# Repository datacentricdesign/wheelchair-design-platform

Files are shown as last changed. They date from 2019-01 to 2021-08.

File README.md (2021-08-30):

# [Wheelchair Design Platform](https://datacentricdesign.github.io/wheelchair-design-platform/)

Welcome!

This repository contains some resources to help designers and developers speak the same language, and work together towards addressing relevant challenges for wheelchair users. It is a collection of workshop materials, code examples and also a compilation of resources to foster a prospering research and design community around wheelchair users.

The best way to explore this repository is through the GitHub Page website: [right here!](https://datacentricdesign.github.io/wheelchair-design-platform/)

# Contributors

Thank you to all the contributors of this project!

(https://github.com/Ryudas)
(https://github.com/dhavalshah02)
(https://github.com/Kattthii)
(https://github.com/jackybourgeois)
(https://github.com/emiliaingemarsdotter)
(https://github.com/cprecioso)
(https://github.com/livein21st)
(https://github.com/gomezago)

# Existing projects

* [The hiking wheelchair](https://github.com/cprecioso/wheelchair-design-platform)
* [The EDU wheelchair](https://github.com/ctsai-1/wheelchair-design-platform)
* [Weelchair tracking for basketball players](https://github.com/FabianIDE/wheelchair-design-platform)
* [Disco Wheelchair](https://github.com/MatthijsBrem/wheelchair-design-platform)
* [Wheelchair Madness 2222](https://github.com/pherkan/wheelchair-design-platform/tree/master/wheelchair)
* [Who is sitting?](https://github.com/Rosanfoppen/wheelchair-design-platform/tree/master/wheelchair)
* [Magic Wheelchair](https://github.com/Yuciena/wheelchair-design-platform)
* [Yoga Wheelchair](https://github.com/artgomad/wheelchair-design-platform)

Feel free to contact us at jacky@datacentricdesign.org. We welcome feedback, pull requests
or links to your project.

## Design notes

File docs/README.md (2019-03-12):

Wheelchair Design Platform is a repository that contains some resources to help
designers and developers speak the same language, and work together towards
addressing relevant challenges for wheelchair users. It is a collection of
workshop materials, code examples and also a compilation of resources to foster
a prospering research and design community around wheelchair users.

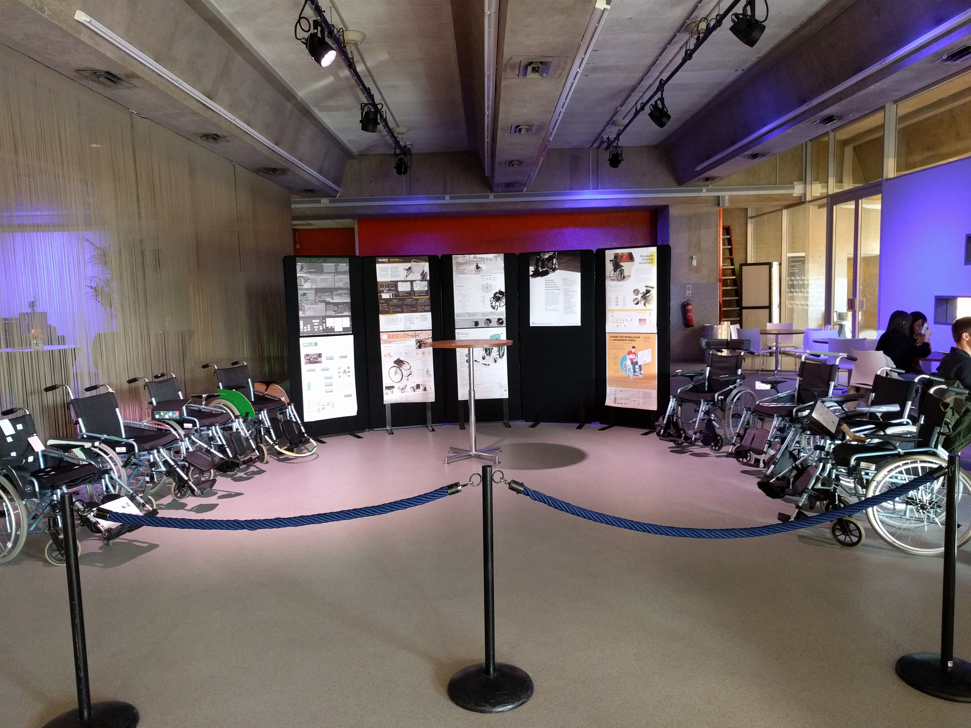
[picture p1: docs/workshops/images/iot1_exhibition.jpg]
IoT1 Exhibition


## Workshops

* [Getting started](workshops/GettingStarted.md)
* [Workshop 1: Building an Internet-Connected Wheelchair](workshops/Workshop1.md)
* [Workshop 2: Integrating and Visualising Sensor-Based Data](workshops/Workshop2.md)
* [Workshop 3: Developing Algorithms and Controlling Actuators](workshops/Workshop3.md)
* [Workshop 4: Developing and Conducting a Data Collection Campaign](workshops/Workshop4.md)
* [Workshop 5: Implementing a Machine Learning Pipeline](workshops/Workshop5.md)
* [Workshop 6: Developing a Product Analytics Dashboard](workshops/Workshop6.md)

## Resources

* This platform uses two programming languages, Python on computers and C on
micro-controllers. While descriptions and examples of code should help you
get started, you can find some additional resources
[here](resources/software.md).

* Documentation of your project is key,
[here are some tips and examples](resources/documentation.md).

* [Git manipulation such as Pull Requests](resources/git.md).

## Main Components

__**Disclaimer:**__ the design of this platform focuses on flexibility and
technology exploration rather than optimization\.

The main design includes a Raspberry Pi 3 and an Arduino Mega 2560 on the wheelchair frame.

The Arduino Mega is the micro-controller of the platform. Fixed on the main frame of the wheelchair,
it can collect data from sensors (e.g. force sensors, accelerometers), and trigger actions from actuators
(e.g. LEDs, vibration motors).

More on the Arduino Mega can be found [here](resources/arduino.md "Arduino resources").

Raspberry Pi is a small computer. It is also fixed to the main frame of the wheelchair,
where it can:
* interact with the Arduino Mega via USB to receive data and transmit commands;
* interact with the Internet to transmit commands and receive data;
* store data locally in files;
* run (machine learning) algorithms.

More on the Raspberry Pi can be found [here](resources/raspberrypi.md "Raspberry Pi resources").

These components fit together as shown on the following diagram. A large powerbank
powers the Raspberry Pi. The Arduino Mega communicates and receives power from the
Raspberry Pi via USB. A Feather (Arduino-like development board) on the wheel connects to
the Raspberry Pi via Bluetooth to sense and actuate from the wheel.

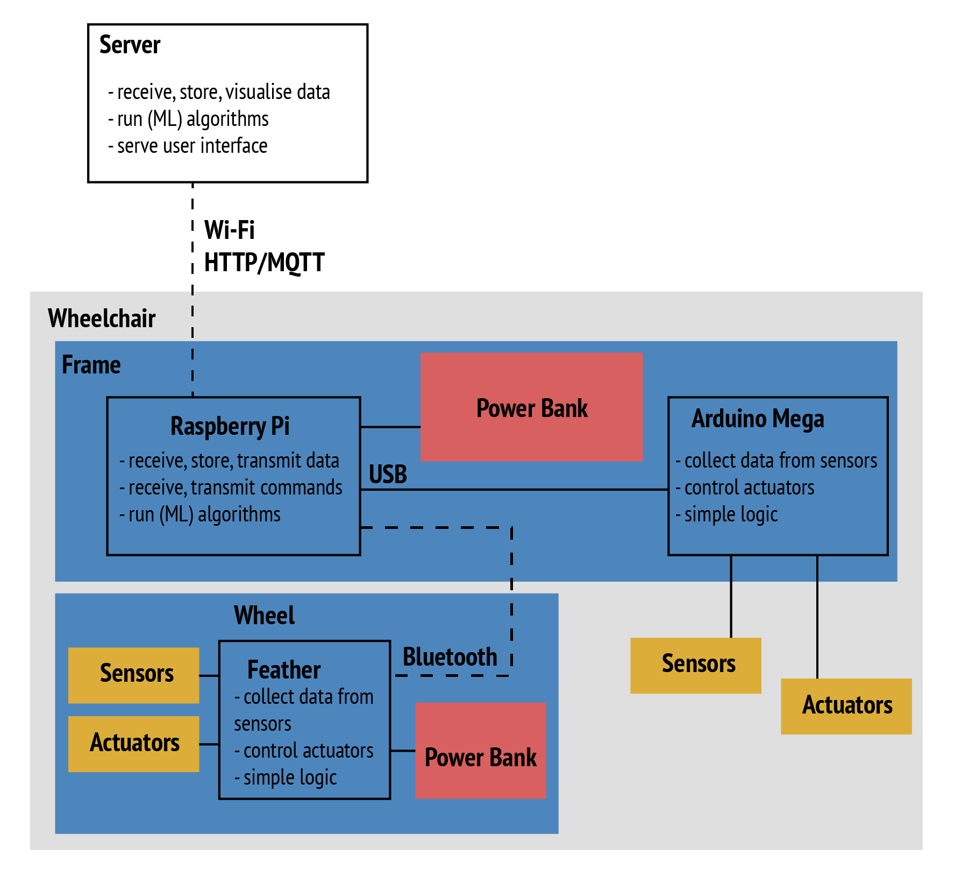
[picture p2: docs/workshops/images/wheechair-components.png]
Main Wheelchair components


## List of suggested components:

On the frame:

* 1 Raspberry Pi 3B+;
* 1 SD card (Some come directly with NOOBS installed);
* 1 Arduino Mega;
* 1 Large power bank;
* 1 large breadboard;
* 1 USB cable A/micro (Powerbank to Raspberry Pi);
* 1 USB cable A/B (Raspberry Pi to Arduino Mega).

On the wheel:

* 1 Feather 32u4 (Bluetooth enabled);
* 1 small power bank;
* 1 small breadboard;
* 1 USB cable A/B (power bank to Arduino Uno).

## Contact and Existing projects

* [The hiking wheelchair](https://github.com/cprecioso/wheelchair-design-platform)
* [The EDU wheelchair](https://github.com/ctsai-1/wheelchair-design-platform)
* [Weelchair tracking for basketball players](https://github.com/FabianIDE/wheelchair-design-platform)
* [Disco Wheelchair](https://github.com/MatthijsBrem/wheelchair-design-platform)
* [Wheelchair Madness 2222](https://github.com/pherkan/wheelchair-design-platform/tree/master/wheelchair)
* [Who is sitting?](https://github.com/Rosanfoppen/wheelchair-design-platform/tree/master/wheelchair)
* [Magic Wheelchair](https://github.com/Yuciena/wheelchair-design-platform)
* [Yoga Wheelchair](https://github.com/artgomad/wheelchair-design-platform)

Feel free to contact us at jacky@datacentricdesign.org. We welcome feedback, pull requests
or links to your project.

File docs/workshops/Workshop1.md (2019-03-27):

# Workshop 1: Building an Internet-connected Wheelchair

In this workshop we lead you step-by-step toward setting up the main components
of the Internet-Connected Wheelchair by getting the code, registering on the cloud
platform, running a Python code and running an Arduino code.

1. [Git Flow](#1-git-flow)
2. [Data-Centric Data Hub](#2-data-centric-design-hub-per-group)
3. [Run Python Example](#3-run-python-example)
4. [Data Collection with Arduino](#4-data-collection-with-arduino)
5. [Setting up the Raspberry Pi](#5-setting-up-the-raspberry-pi)

# 1 Git Flow

### 1.1 Fork Wheelchair Design Platform repository (only one member of the group)

*'A fork is a copy of a repository. Forking a repository allows you to freely
experiment with changes without affecting the original project.'*
<a href="https://help.github.com/articles/fork-a-repo/" target="_blank">(GitHub Help)</a>

Go to the GitHub repository of the Wheelchair Design Platform:
<a href="https://github.com/datacentricdesign/wheelchair-design-platform" target="_blank">https://github.com/datacentricdesign/wheelchair-design-platform</a>

On the top-right corner of this GitHub page, click on Fork.

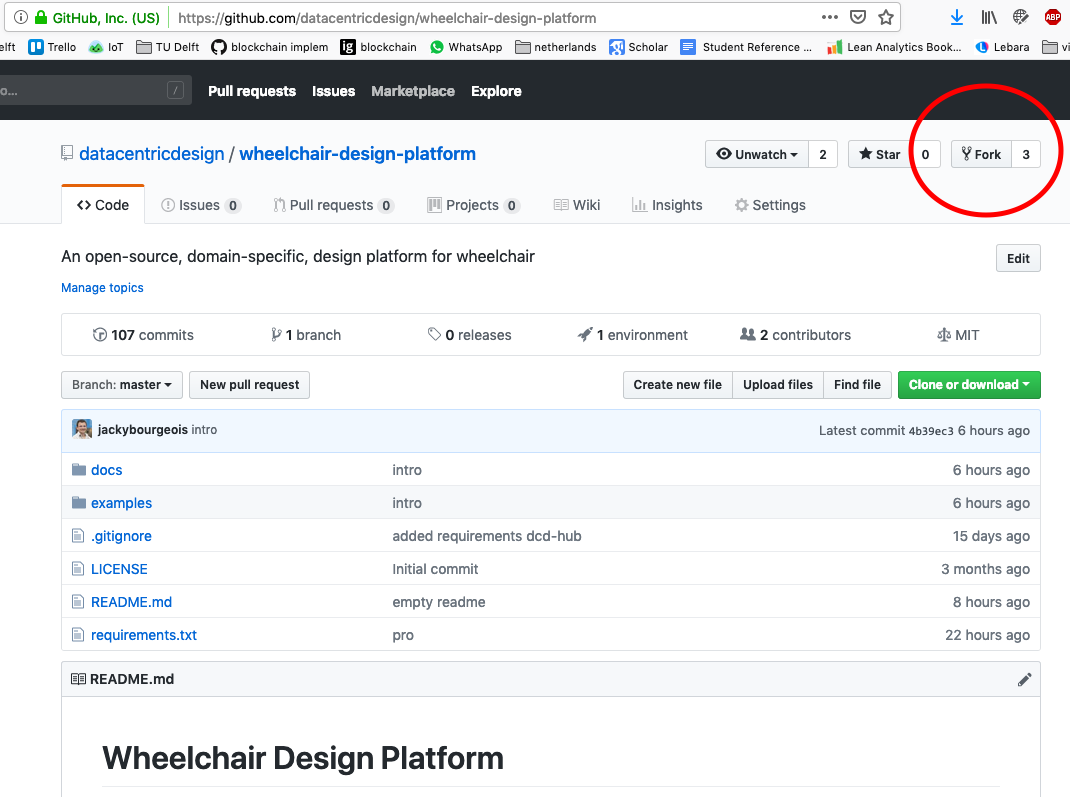
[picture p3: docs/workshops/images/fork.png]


In the dialog, select your account (where you create the copy of the repository).

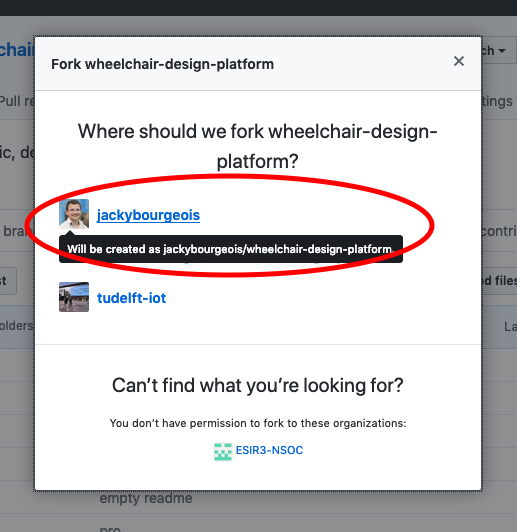
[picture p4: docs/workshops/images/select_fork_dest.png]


You now have a copy of the wheelchair-design-platform repository on your own account.

### 1.2 Add members to repo (only one member of the group)

Your repository is publicly accessible for reading. However, you need to give
the other members of the group access to this repository. On the top menu, click
*'Settings' > 'Collaborators'*. Search the username of your group members and add them.

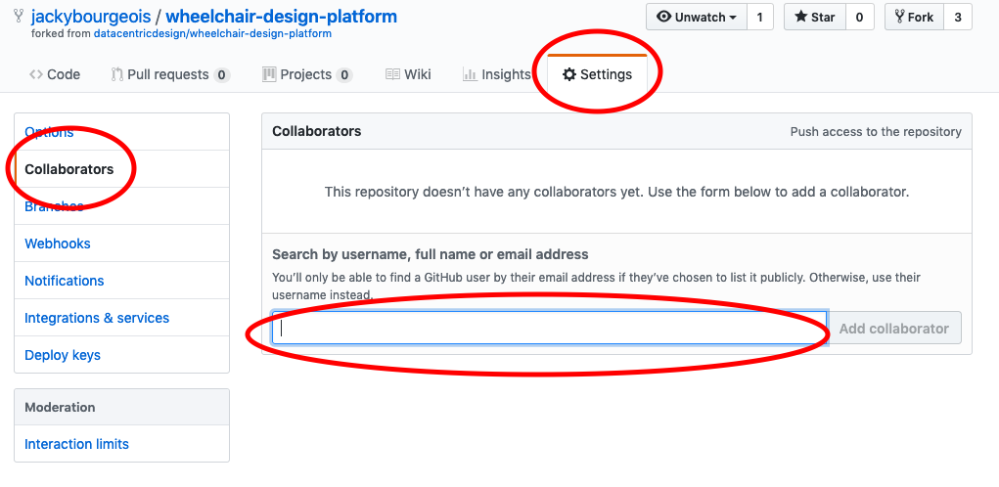
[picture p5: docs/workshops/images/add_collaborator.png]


### 1.3 Create a project (only one member of the group)

GitHub offers a convenient way of managing your projects with a Kanban (scheduling system) style
board. On the top menu, click on 'Projects' and click on the green button 'New
Project'. Fill in a project name, select the template 'Basic Kanban' and click
'Create project'. You can use this space to map your tasks and your progress.

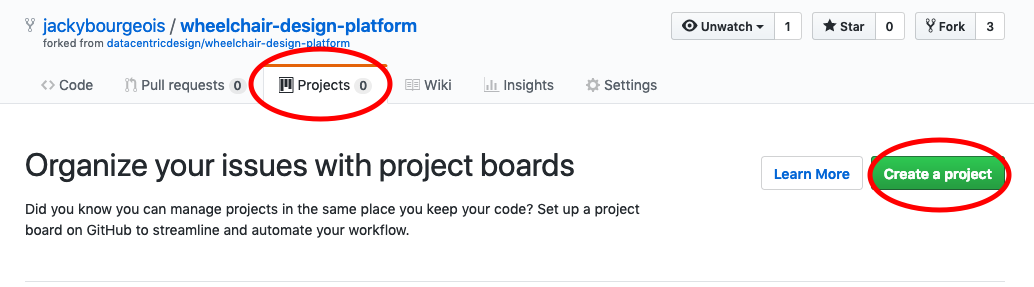
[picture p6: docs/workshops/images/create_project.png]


### 1.4 Clone repository (all group members)

*'When you create a repository on GitHub, it exists as a remote repository. You
can clone your repository to create a local copy on your computer and sync
between the two locations.'*
<a href="https://help.github.com/articles/cloning-a-repository/" target="_blank">(GitHub Help)</a>

On GitHub, at the top of your forked repository, click on the green button 'Clone or
download' and copy the provided link.

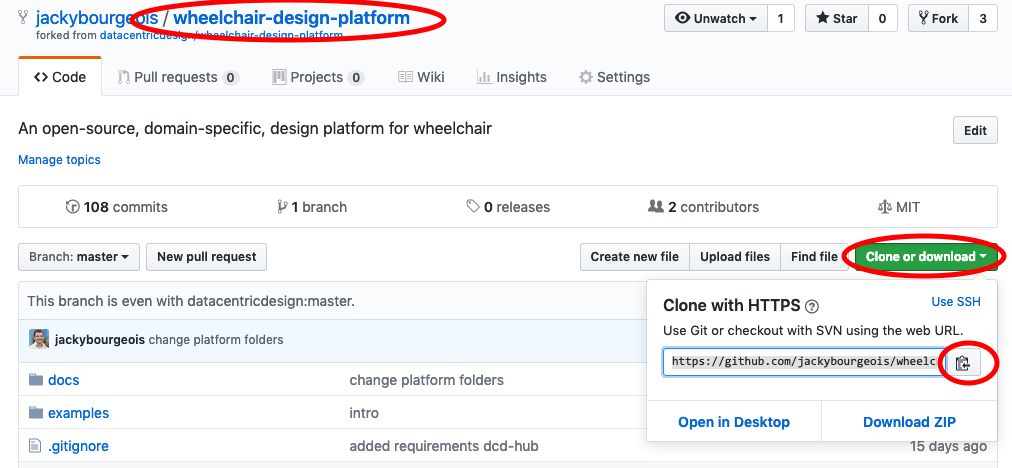
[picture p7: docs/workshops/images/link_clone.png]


Go back to the Atom terminal, and type 'git clone' followed by the link you copied.
For example:

```bash
git clone https://github.com/example/wheelchair-design-platform.git
```

Flowchart Push Button

Let's tell Git who we are, by typing the following commands (enter these commands one after the other):

```bash
git config --global user.email "YOUR EMAIL ADDRESS"
git config --global user.name "YOUR NAME"
```

## 1.5 Project in Atom

To open the project you cloned, click on 'File' > 'Open Folder' on the top menu and
select the folder you cloned. On the left panel, you can see the files of your
project.

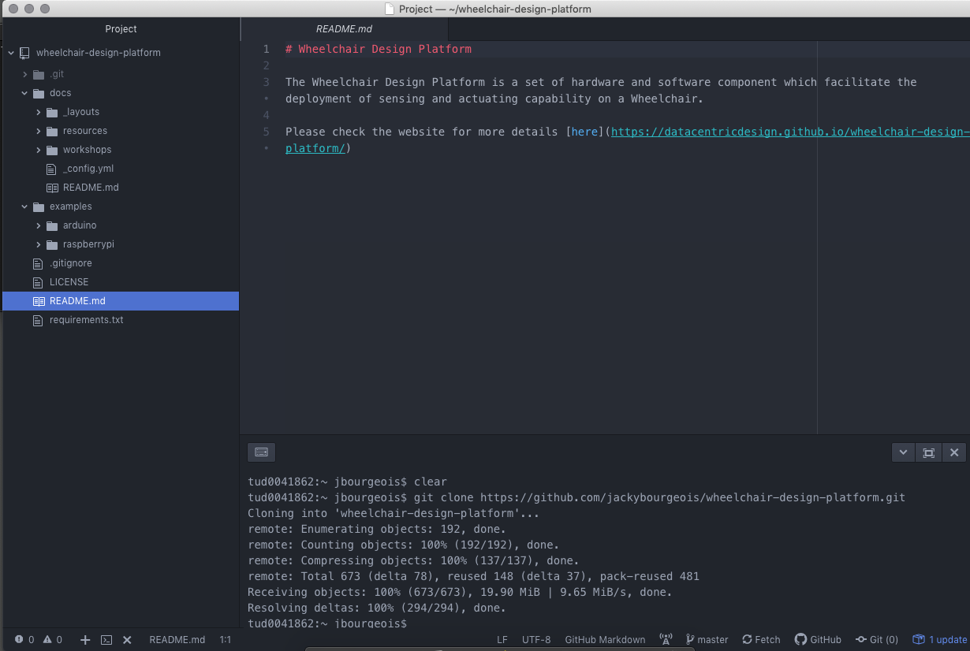
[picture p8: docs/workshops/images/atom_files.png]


Let's have a closer look:

* The .git folder contains the full history of your project, managed by git. Do not
edit or delete files in this folder;
* The docs folder contains documentation and workshops;
* examples contains all code examples to get started;
* .gitignore contains the list of files/file extensions you do not want to track
with Git. It is especially convenient for local configuration or passwords not
to be shared;
* LICENSE contains the MIT license for this project;
* README.md contains a short introduction to the platform in Markdown. Markdown
is a lightweight markup language, i.e. minimal set tags to format text;
* requirements.txt contains the list of the python libraries you need to install for
the project to work;

## 1.6 Sign up on the Data-Centric Design Hub

We now want to register an account for a cloud service. We will use the prototype
from TU Delft IDE's Faculty of the Data-Centric Design Hub. Go to <a href="https://dwd.tudelft.nl/manager" target="_blank">https://dwd.tudelft.nl/manager</a>

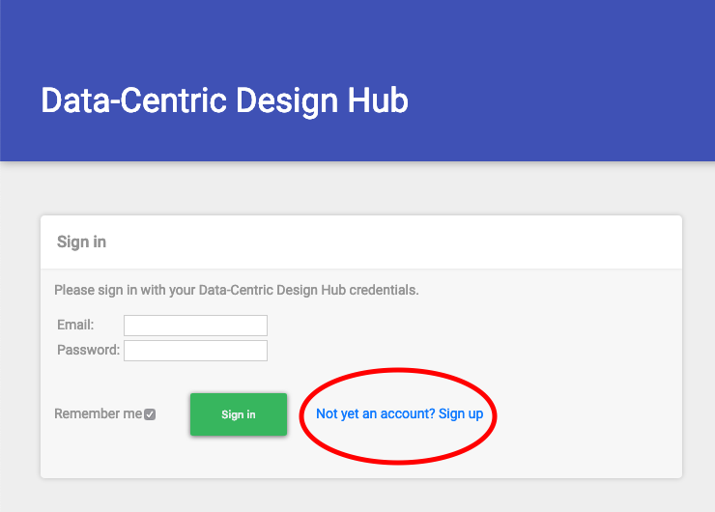
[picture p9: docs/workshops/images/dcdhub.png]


Sign up as a group with an email address, a name and a password.

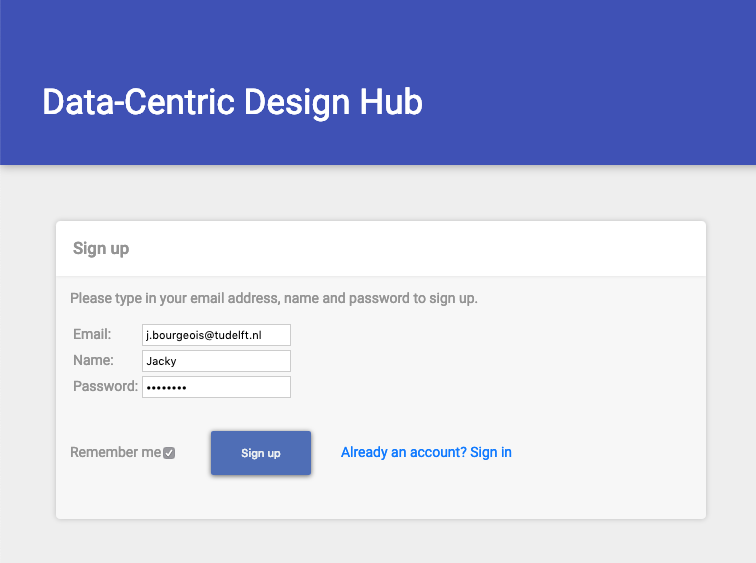
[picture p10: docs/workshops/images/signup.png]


The sign up process creates an account, then the standard OAuth2 process starts
with a consent: you need to let the manager access your Things, so that it can
help you manage them. To do so click "Allow access".

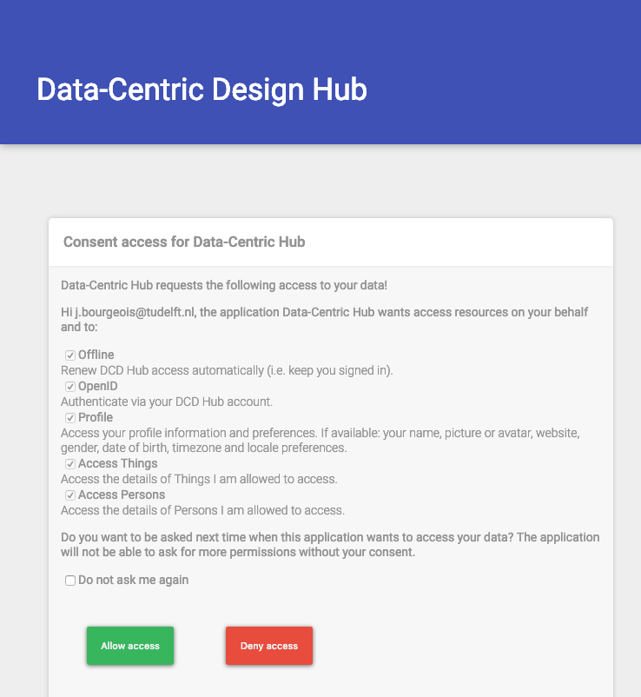
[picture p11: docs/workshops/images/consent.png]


Once the consent succeeded, you can click on 'My Things' and create a first one.
For example with the name 'My wheelchair', type 'Wheelchair', and a
description 'An Internet-connected wheelchair'.

The process may take a few seconds, as the hub generates an access token for your Thing.

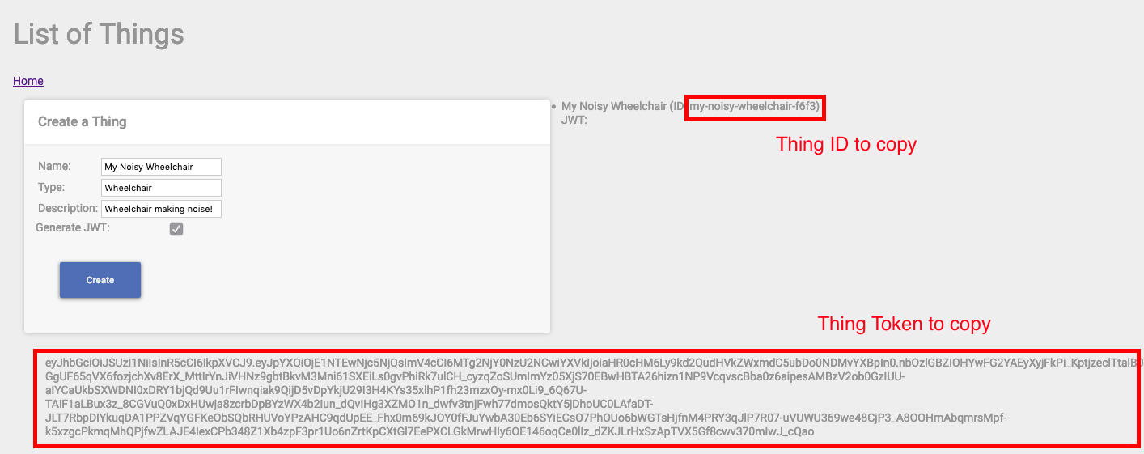
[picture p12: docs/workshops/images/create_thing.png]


**COPY AND SAVE THIS TOKEN** in a text file, it will be shown only once and enables
your wheelchair to communicate with the hub. You can also save the thing id, but
you can always go back to the manager to retrieve this id.

Back to Atom and your project, let's create a first Python example.

## 3 Run Python Example

### 3.1 Dependencies

We use Pip to install the dependencies we need, listed in the file requirements.txt.
This file contains a dependence to the library writen for the Data-Centric Design
Hub as well as the a dependence for MQTT, a communication protocol we use to
talk to the hub.

Open the Atom terminal ('plus' sign in the bottom-left corner) and execute the following command.

On Mac:

```bash
pip3 install -r requirements.txt --user
```
On Windows:

```bash
python -m pip install -r requirements.txt --user
```

Here we 'install' the Python dependencies for our project. The option -r indicates we provide a file name that contains
the required dependencies, the option --user indicates we install the dependencies
in a dependency folder specific for the current users.

## 3.2 Environment Variables

On the left panel, right-click on the root folder "wheelchair-design-platform" > New Folder and name it 'wheelchair'.

Copy the file examples > raspberrypi > get_started.py
in your 'wheelchair' folder.

Opening this file, this Python code import the necessary library, then we can see
the following lines:

```python
THING_ID = os.environ['THING_ID']
THING_TOKEN = os.environ['THING_TOKEN']
```

In Python, it means we look at the environment variables to read the id and
access token of our thing. To provide these information as environment variable,
right click at the root of your project (left panel) and create a file '.env'.

In this file, type in the following and paste your id and access token after
the equal signs.

```bash
THING_ID=
THING_TOKEN=
```

Note: We do not want to track the file '.env' with Git as it contains secrets. To
avoid any mistake, the file .gitignore list all files, folders and extensions to
ignore. You will find '.env' in the list.

## 3.3 Read through the Python Code

Going back to the get_started.py Python script, read through the code and comments
to capture the main steps:

* Create and connect a Thing to the Hub
* Retrieve and display the Thing details
* If the Thing is not containing any property, create a dumb property
* In any case, retrieve this dumb property
* Continuously call a method that generate dumb data and send them to the hub

Here are a few Python elements to note:

* Use # in Python to comment your code
* my_thing and my_property are variables
* To display information in the terminal, we use the method print()

```python
print("show text")
```

* Conditional statement: In Python we express the condition with 'if', elif
(else if) and else (more details
<a href="https://www.tutorialspoint.com/python/python_if_else.htm" target="_blank">here</a>.

In our case, we check if the thing details we retrieved from the server has no property
(a newly created Thing) and then create a dumb property.

```python
if len(my_thing.properties) == 0:
    # create a dumb property
```

* Indentation is key in Python. Take the previous example of condition, the indentation
defines what is in the condition. Any following line aligned with the if would be
considered outside the condition.

## 3.4 Execute the Python code

Let's execute this code. Go to the Atom terminal and type in the following command:

On Mac:

```bash
python3 wheelchair/get_started.py
```

On Windows:

```bash
python wheelchair\get_started.py
```

If the example runs properly you should see a log generated every two seconds,
indicating dumb data is being sent to the Hub.

## 3.5 Visualise Data on Grafana

To visualise this data, we use Grafana.

Go to the <a href="https://dwd.tudelft.nl/grafana" target="_blank">dwd.tudelft.nl/grafana</a>,
sign in with the provided login and password.

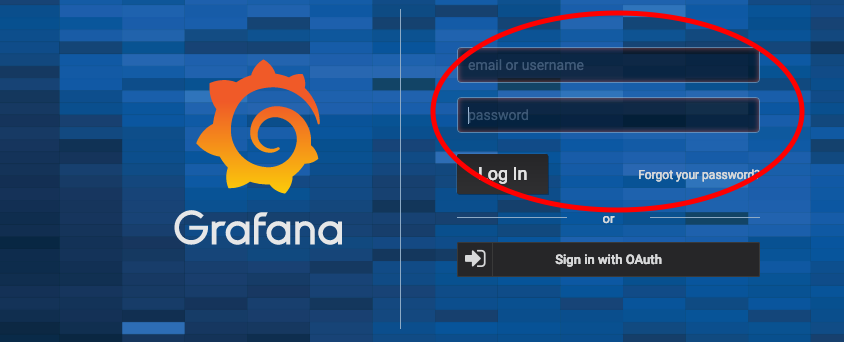
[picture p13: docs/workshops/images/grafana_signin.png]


Click on the plus on the left panel.

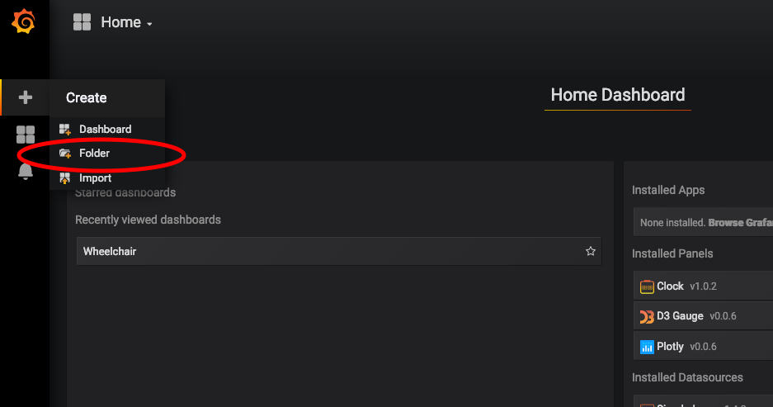
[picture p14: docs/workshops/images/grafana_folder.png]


Create a new folder for your project.

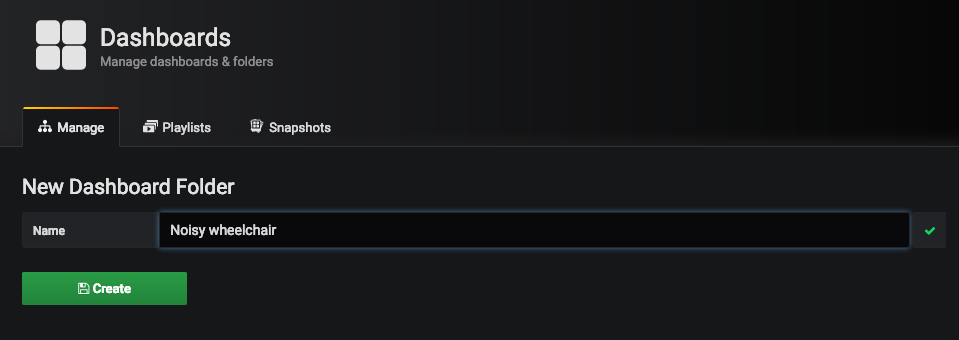
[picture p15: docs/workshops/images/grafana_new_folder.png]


Then, click on the green button 'New Dashboard' to create a new Dashboard, and
select a new panel 'Graph'.

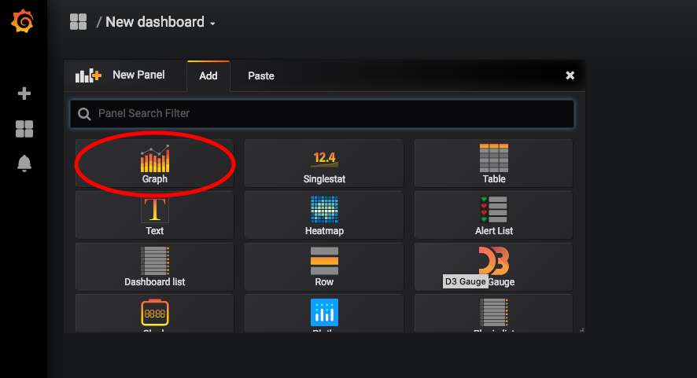
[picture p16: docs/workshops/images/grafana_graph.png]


At the top of this new panel, click on 'Panel Title > Edit'

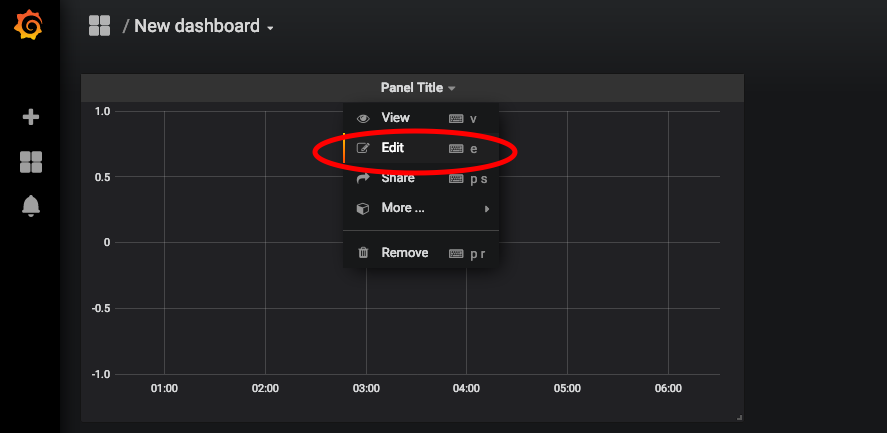
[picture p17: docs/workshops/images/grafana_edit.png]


At the bottom, in the query element GROUP BY, click on time and 'remove'.

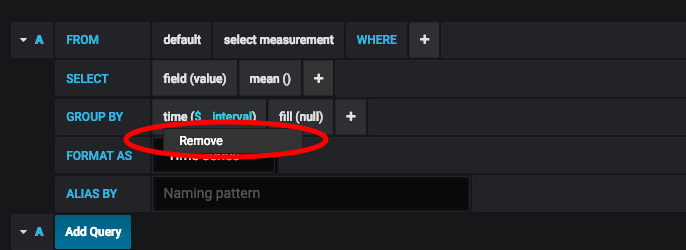
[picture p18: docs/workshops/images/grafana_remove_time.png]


In FROM, click on 'Select Measurement' and select your Property ID. If your
Property ID is not appearing in the list, the hub is not receiving data from
your python code.

In SELECT, click on field and select Value1. Then click on the
plus > Fields > Field to add Value2 and Value3.

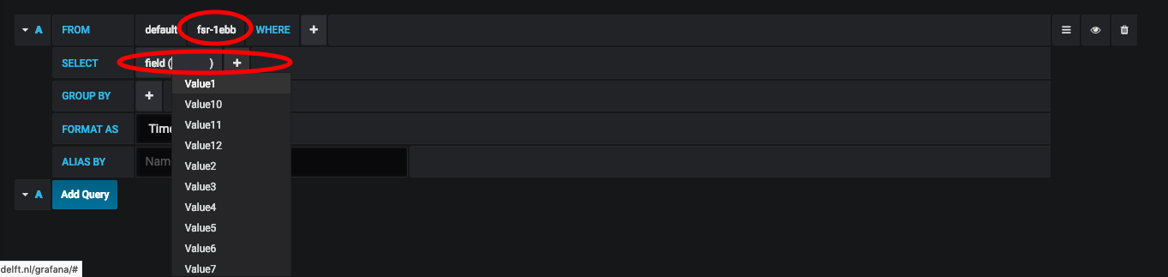
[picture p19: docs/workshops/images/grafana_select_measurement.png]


Back in the Atom terminal, stop your Python script with CMD+C (Ctrl+C).

# 4 Data Collection with Arduino

In this section we will log short and long press events of a push
button. It highlights that a sensor-based data point can be as simple as a button
event and tell us about how a user make use of it.

## 4.1 Push Button Example

In Atom, copy the folder examples > arduino > push_button_led_log
in your 'wheelchair' folder. Then, open this folder in Arduino IDE.

Looking at the code, we recognise the Arduino-like structure in three blocks:

* Declaration of variables and libraries, available throughout the code.
Note by convention, the constants are in uppercase (variables that will not change
during the programme) while other variables are in lowercase.

```cpp
int BUTTON_PIN = 22; // choose the input pin for the push button
int LED_PIN = 13;    // Choose the output pin for the LED

long LONG_PRESS_TIME = 500; // How long is a 'long press' (minimum, in ms)

long buttonActiveSince = 0; // Since when the button has been pressed (in ms since Arduino started)
boolean longPressActive = false; // Are we currently in a 'long press' event
```

* The setup() method executed once when the Arduino starts;

```cpp
void setup() {
  pinMode(BUTTON_PIN, INPUT);    // declare pushbutton as input
  pinMode(LED_PIN, OUTPUT);      // declare LED as input

  Serial.begin(9600); // setting baud speed for Serial (a baud is a pulse)

}
```

* The Loop() method executed infinitely after the setup method.
**WARNING** -  make sure to replace MY_PROPERTY_ID in this example with the ID of a property you created in Data-Centric Design hub.

```cpp
void loop() {
  // Is button active?
  if (digitalRead(button) == LOW) {
    // if the button was not yet pressed
    if (buttonActiveSince == 0) {
        buttonActiveSince = millis();
    } else if ((millis() - buttonActiveSince > LONG_PRESS_TIME)
                && longPressActive == false) {
          longPressActive = true;
          digitalWrite(led, HIGH);  // turn LED ON
        }
    }

  // Was button active?
  } else {
    // Was Long Press event?
    if (buttonActiveSince > 0) {
      // End Long Press event
      if (longPressActive == true) {
        Serial.println("MY_PROPERTY_ID,2");
        digitalWrite(led, LOW);  // turn LED OFF
        longPressActive = false;

      // End Short Press event
      } else {
        Serial.println("MY_PROPERTY_ID,1");
      }
      buttonActiveSince = 0;
    }
  }

}
```

In this example, we want to detect when a push button is pressed. We will trigger
two type of events when the button is released: 'short' or 'long' press.

The following flow chart illustrates the algorithm of this example code.

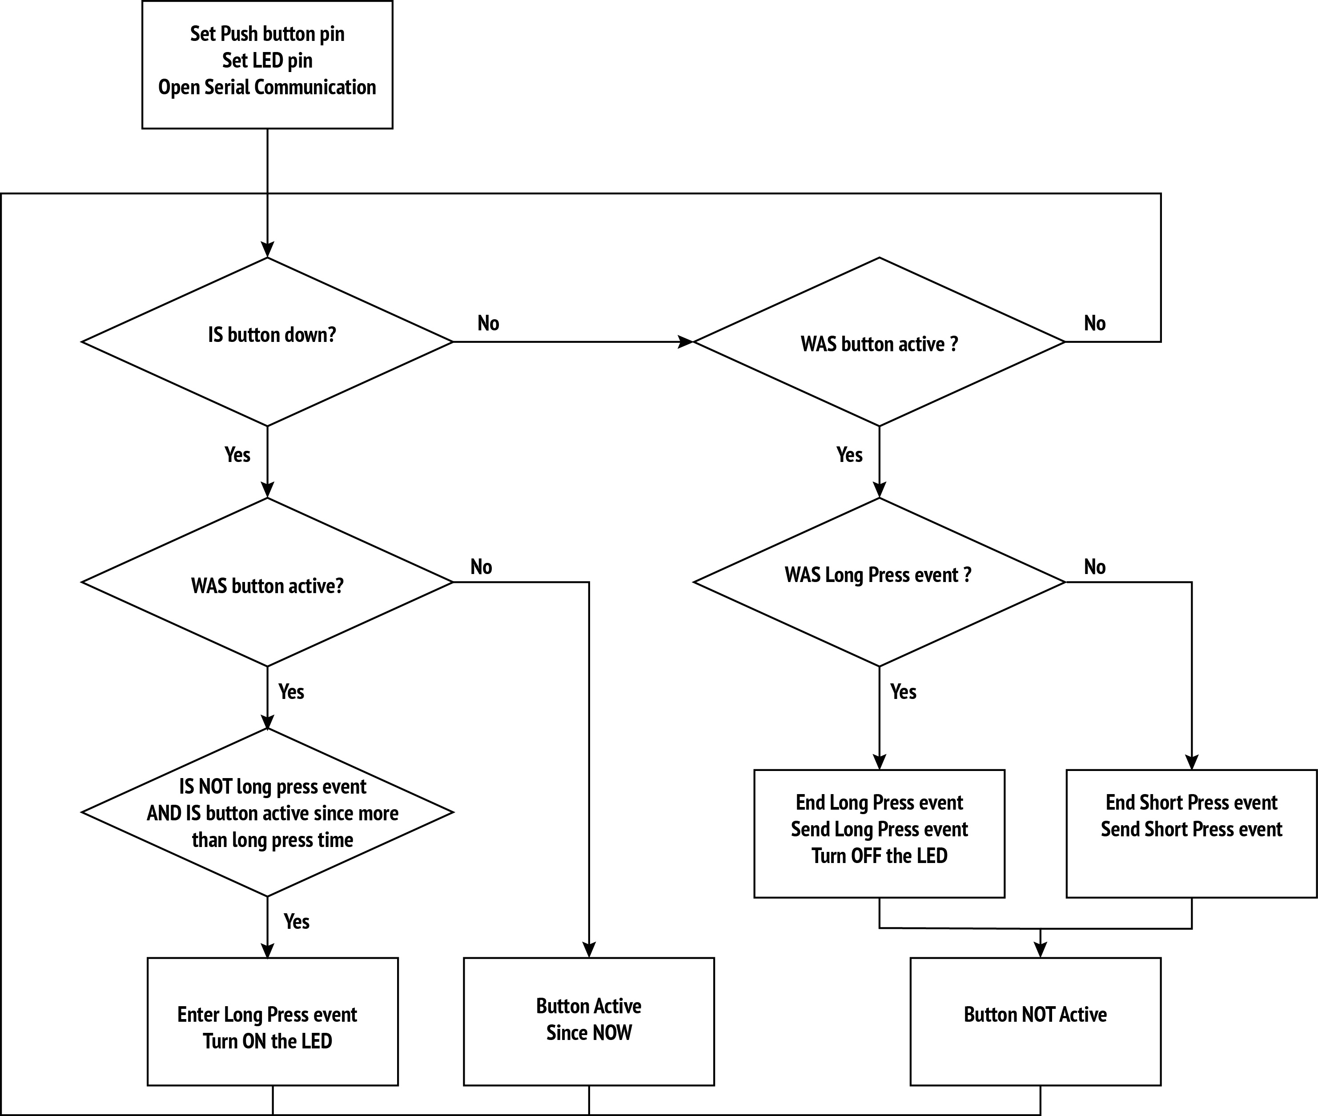
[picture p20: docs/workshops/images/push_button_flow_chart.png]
Flowchart Push Button


In the Arduino IDE, go in the top menu 'Tools > Boards', and  select 'Arduino/Genuino Mega or Mega 2560'

Then press the Verify button (green circle with tick).

## 4.2 Wire Push Button and LED

In this example we need three wires, a resistor, an LED and a push button.

Flowchart Push Button

## 4.3 Connect Arduino

Use the USB cable to connect the Arduino to your laptop.

In Arduino IDE, in the top menu Tools > Port select your Arduino

Then press the Flash button to send the code into the Arduino (green circle with right arrow)

In the Arduino IDE, in the top menu 'Tools' open the 'Serial Monitor'.
Look at the input, pressing the push button should turn on the LED and produce a
log in the Serial Monitor.

## 4.4 Update Python Example

The last step is to adapt the Python code on your laptop to read the Serial input
from the Arduino and forward them to the Data-Centric Design Hub.

You can copy the code from examples/serial_example.py in your wheelchair folder.

In this code, we use the environment variable again to provide the thing id and token.

We need an extra environment variable(SERIAL) to specify the serial port. You can find
the port name for it on the Arduino IDE, in the top menu Tools > Ports. For example:

```bash
THING_ID=
THING_TOKEN=
SERIAL=MY_PORT_NAME
```

We are now ready to run the Python code

On Mac

```bash
python3 wheelchair/serial_example.py
```

On Windows

```bash
python wheelchair\serial_example.py
```

Go back to Grafana to visualise the inputs

# 5 Setting up the Raspberry Pi

The next step consists in setting up the RaspberryPi and running your code on it.

Insert the SD card in your laptop.

## 5.1 Set up an empty SD Card

__**(Skip this section if you have an SD Card with NOOBS pre-installed)**__

Download and install the software

Get the latest Raspbian here: https://www.raspberrypi.org/downloads/raspbian/

Unzip the file, you obtain an image file (extension .img)

To install this image on the SD card, download and install Etcher: https://www.balena.io/etcher/

Starting Etcher, you first select your image file, then your SD card, and 'Flash'.

# 5.2 Getting Started without Monitor

### 5.2.1 SSH

To connect to the Raspberry Pi without monitor, mouse and keyboard, we use directly
your laptop. To do this, we need to enable the 'ssh' protocol (for Secure Shell)
on the  Raspberry Pi. This protocol gives us the possibility to remotely access
a computer through the network. On your laptop, open text editor (TextEdit on Mac,
Editor on Windows) and save an empty file named 'ssh' (without extension) at the
root of the 'boot' disk (SD card). This file will indicate that we want to enable ssh.

### 5.2.2 Network Access

To connect your Raspberry Pi to the network, create a second file
'wpa_supplicant.conf' with the following content:

```bash
country=NL
update_config=1
ctrl_interface=/var/run/wpa_supplicant

network={
  ssid="YOUR_NETWORK_SSID"
  psk="YOUR_NETORK_PASSWORD"
}

```

Save this file on the 'boot' partition. Make sure that its extension is .conf rather
than .conf.txt (most texts editor will automatically add .txt or .rtf and hide it,
double-check that your file is not recognised as a text document).

To connect to Eduroam:

```bash
network={
  scan_ssid=0
  ssid="eduroam"
  key_mgmt=WPA-EAP
  eap=PEAP
  phase2="MSCHAPV2"
  identity="YOUR_EDUROAM_NETID"
  password="YOUR_EDUROAM_PASSWORD"
}
```

__**Disclaimer**__: this process requires to insert the Eduroam password. Thus, it is
important to protect the access to your Raspberry Pi. Make sure you apply ALL the
following steps marked as __**SECURITY**__

__**SECURITY**__ Disable auto-login: by default, anyone with an HDMI cable can look at
your Raspberry Pi and its files. Disable this feature

### 5.3 Booting and Connecting

__**DISCLAIMER:**__ If you do this workshop as part of a class, keep in mind that
all Raspberry Pi will have the same name on the network. You will have to power
your Raspberry Pi one after the other to be able to identify them.

Eject the SD card and insert it in on the Raspberry Pi, then power the Pi.

If the settings are correct, it takes about 30 seconds to get the Raspberry Pi on
the network. Make sure your laptop is connected to the same network, then connect
via ssh with the following command.

On Windows, you need to search for Windows Powershell and type the below command in there

On Mac

```bash
ssh pi@raspberrypi.local
```

In this command, 'pi' is the default username and raspberry.local is your default hostname (the
name of the Pi on the local network). You should type in your own username and hostname if you have changed it.

First you will need to type in 'yes' followed by Enter.

Then, you will be prompt for the default password. Type in 'raspberry'. Note:
when you type in the password, no letter appears in the terminal. This is the
normal behaviour to protect your password.

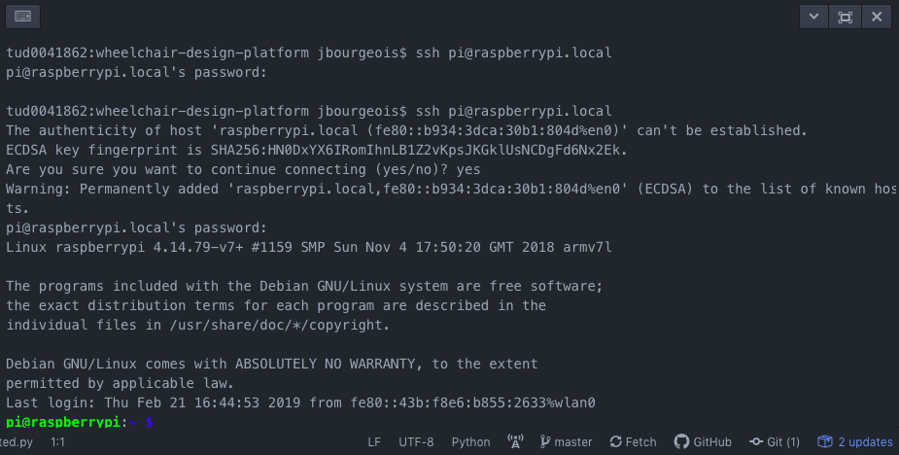
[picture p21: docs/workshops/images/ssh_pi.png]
SSH Pi


Once connected, we want to change the hostname, i.e. the name of your Raspberry Pi
on the network. By default, it is 'raspberrypi' which is not practical while you
have several of them (like in a classroom setting). To do this, we need to edit
two files /etc/hostname and /etc/hosts. We use the editor nano for this.

Type in:

```bash
sudo nano /etc/hostname
```

This command opens the file /etc/hostname in nano. Replace 'raspberrypi' with the
name of your choice (without space). In the following example, we use the
hostname 'noisy-wheelchair'.

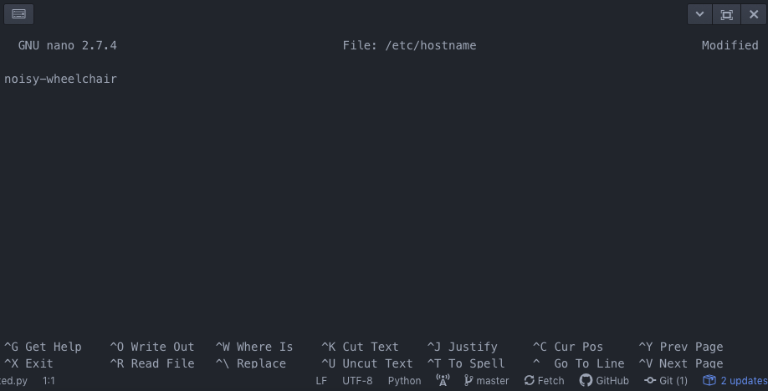
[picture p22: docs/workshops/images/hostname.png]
Hostname


To save and exist, press Ctrl+X, press Y ()to answer 'Yes' to the question) followed
by Enter. Similarly, edit the file /etc/hosts and change 'raspberrypi' for the
same name, e.g. 'noisy-wheelchair'.

```bash
sudo nano /etc/hosts
```

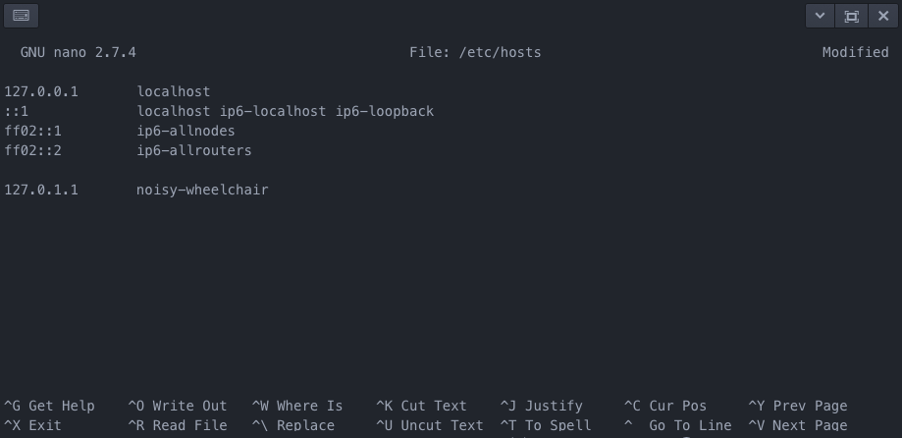
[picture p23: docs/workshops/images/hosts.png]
Hosts


Again, save and exit with Ctrl+X, then Y followed by Enter.

Reboot your Rasberry Pi with:

```bash
sudo reboot
```

After about 30 second, you should be able to connect to you Raspberry Pi with
your new hostname. For example:

```bash
ssh pi@noisy-wheelchair.local
```

__**SECURITY**__ Next, we want to change the user password: changing the
default password 'raspberry' gives you more guaranty you are the only one
accessing your Raspberry Pi.

```
sudo passwd
```

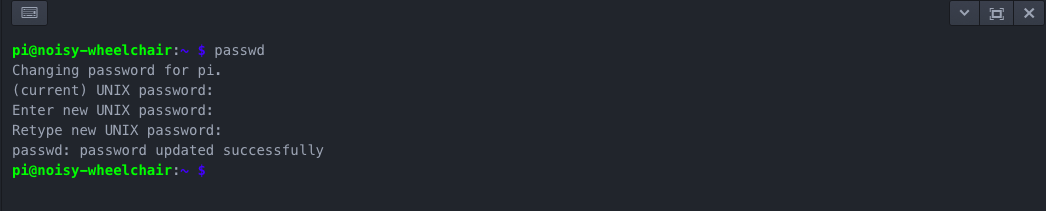
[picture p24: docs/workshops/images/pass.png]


### 5.4 Installing Requirements

First, we need to update the Raspberry Pi with the latest version of its software.

```bash
sudo apt-get update
sudo apt-get upgrade
```

Set up Git

```bash
sudo apt-get install git
```

Clone your GitHub repository. Similarly to step 1.4, we now clone your repository.
This time, we clone it on the Raspberry Pi. For example:

```bash
git clone https://github.com/example/wheelchair-design-platform.git
```

In the terminal, to navigate through folder we use 'cd'. Enter the folder you have just
cloned with:

```bash
cd wheelchair-design-platform
```

Then, we need to create an .env file, in the project folder, with  THING_ID, the THING_TOKEN and the
SERIAL port.

```bash
nano .env
```

Copy your thing id and token, and use /dev/ttyUSB0 as a serial port (there are other serial ports on your raspberry pi you can try, such as ttyS0, ttyAM0).

Change password

Install the requirements with Pip

```bash
python3 -m pip install -r requirements.txt --user
```

```bash
python3 wheelchair/serial_example.py
```

The result should be the same as running it on your laptop.

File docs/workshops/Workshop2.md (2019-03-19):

# Workshop 2: Integrating and Visualising Sensor-Based Data

In this workshop we lead you setp-by-step to experience the capabilities of an 
orientation sensor and set it up on a wheel as a Bluetooth service.

1. [Orientation Sensor](#1-orientation-sensors)
2. [Feather Bluefruit](#2-feather-bluefruit)
3. [Bluetooth Low Energy (BLE) GATT Service](#3-bluetooth-low-energy-ble-gatt-service)
4. [Local Pre-Processing](#4-local-pre-processing)

## 1 Orientation Sensors

To get started with this second workshop, we propose to experience the principles
 and the capabilities of an orientation sensors. Go through the explanation and
 the examples we compiled for the BNO055: [Orientation Sensor](../resources/sensors/orientation.md)

## 2 Feather Bluefruit

With a better understanding of the BNO055, we can now apply these example on our
wheelchair to monitor the various movement of the wheel. As this part of the wheelchair
is mobile, we need a wireless connection to transmit information.

At this stage, there are three potential strategy:
1. Sending data directly to the cloud, via LoRa, 4G or WiFi;
2. Sending data to the Arduino Mega by setting up a Personal Area Network (PAN),
e.g. Bluetooth, Zwave, Zigbee.
3. Sending data to the Raspberry via WiFi or Bluetooth (Wireless capabilities of the Pi).

In this workshop we choose the third option, sending data to the Raspberry Pi via
Bluetooth. This strategy avoid implementing Bluetooth on the Arduino Mega, leveraging
the Raspberry Pi capabilities. We  also centralise the data before sending them
to the cloud, offering more flexibility.

On the wheel, we propose to implement the Feather 32u4, an Arduino-like, Bluetooth
enabled board by AdaFruit. Have a look at the documentation we compiled to get
an overview of its capabilities and set up your Arduino IDE: [Feather 32u4](../resources/feather.md)

For this you will also have to install the following library (Bluefruit nRF51), which you can do in Sketch -> Include Library -> Manage Libraries :



## 3 Bluetooth Low Energy (BLE) GATT Service

As described in its resource page, the Feather 32u4 has a Bluetooth Low Energy (BLE)
communication capability. To communicate over BLE, we choose the GATT specification
(standing for Generic ATTribute Profile). It is implemented by most Bluetooth
consumer product and will enable our prototype to easily fit in its technology
landscape.

### 3.1 Exploring the Heart Rate Measurement (HRM) GATT Service

Let's run the example of GATT service Heart Rate Measurement (HRM) provided by Adafruit.
It is used by FitBits and alike to send HRM data to your phone.

Back to Arduino IDE, in the top menu select File > Examples > Adafruit BluefruitLE nRF51 > heartratemonitor.

At line 111, change the name 'Bluefruit HRM' to the name of your choice. This will
be the name of your device on the network.

Flash the code on the the Feather 32u4 and open the Serial monitor to observe
the initialisation process.

On your phone, search for 'ble gatt' in the app store and install 'nRF Connect'.
Open the app and scan for devices. The name you gave to your Feather 32u4 should
appear in the list. Click 'Connect' to connect on your Feather 32u4. The list of
GATT services should appear, including the Heart Rate Measurement. Click to open
this service and list its characteristic. Click on the triple arrow down to subscribe
to the Heart Rate Measurement characteristic. You should see the (random) heart
rate value sent by your Feather 32u4 every seconds.

We note the UUIDs of the service and characteristic (standing for Universally Unique
IDentifier), which are part of the standard GATT specification. In the next section
we will choose our own UUID for the orientation service because there is no specification
for such sensor.

### 3.2 Orientation data as GATT Service

Like most connected devices, the Feather rely on the
<a href="https://en.wikipedia.org/wiki/Hayes_command_set" target="_blank">Hayes commands</a>
to communicate over Bluetooth. These commands start with 'AT+'.

To implement a GATT service, the Feather 32u4 as a set of
<a href="https://learn.adafruit.com/introducing-adafruit-ble-bluetooth-low-energy-friend/ble-gatt" target="_blank">AT commands available</a>.
We will walk you through them as we transform the HRM example into an Orientation
GATT service.

At the top, we need extra libraries.

```cpp
#include <Wire.h>
#include <Adafruit_Sensor.h>
#include <Adafruit_BNO055.h>
#include <utility/imumaths.h>
```

We __**add**__ a sample rate to which we will send the orientation data (e.g. 200ms)
and we get the pointer to our BNO055 sensor.

```cpp
#define BNO055_SAMPLERATE_DELAY_MS (200)
Adafruit_BNO055 bno = Adafruit_BNO055(55);
```

We __**update**__ the name of the variable to avoid confusion. Instead of HRM we
have an IMU service and an orientation characteristic.

```cpp
int32_t imuServiceId;
int32_t orientationCharId;
```

We __**add**__ a method to initialise the BNO055.

```cpp
// Initializes BNO055 sensor
void initSensor(void) {
  if(!bno.begin()) {
    error(F("No BNO055 detected. Check your wiring or I2C ADDR!"));
  }
  delay(1000);
  bno.setExtCrystalUse(true);
}
```

At the beginning of setup(), we need to call this initSensor() so that our BNO055
is ready. Note that, the very first line of setup, stops the connection from happening if the Serial console is not open (you can comment this out to stop this behaviour):
``` c++
  while(!Serial); 
  
   // Setup the BNO055 sensor
  initSensor();
```

At this stage, we __**update**__ the AT commands that setup our GATT service. first, we
change the device name to fit its purpose with AT+GAPDEVNAME.

```cpp
  if (! ble.sendCommandCheckOK(F("AT+GAPDEVNAME=Noisy Left Wheel")) ) {
    error(F("Could not set device name."));
  }
```

We __**update**__ AT+GATTADDSERVICE so that we no longer add an Heart Rate Measurment
service, but instead a custom service for our orientation sensor.

Here we choose the a 'random' UUID, which is any chain of 32 hexadecimal characters
(numbers and letters from A to F) that is not yet in the specification. We also
use __**UUID128**__ instead of __**UUID**__ to specify the 32 characters. This contrasts
with HRM, a service that is part of the GATT specification, and does not require the full
UUID.

```cpp
success = ble.sendCommandWithIntReply( F("AT+GATTADDSERVICE=UUID128=00-11-00-11-44-55-66-77-88-99-AA-BB-CC-DD-EE-FF"), &imuServiceId);
```

Similarly, we __**update**__ AT+GATTADDCHAR with a 'random' UUID.

* PROPERTIES 0x10 means it is an notification characteristic, to be subscribed
* MIN_LEN and MAX_LEN are the min and max number of bytes to be sent. A character
in encoded on 1 byte. We want to send data as a string of character such as
-0.00,-0.00,-.00 which represents 17 characters.
* VALUE is the default value sent when subscribing, in our case an empty string.

```cpp
  success = ble.sendCommandWithIntReply( F("AT+GATTADDCHAR=UUID128=02-11-88-33-44-55-66-77-88-99-AA-BB-CC-DD-EE-FF,PROPERTIES=0x10,MIN_LEN=1,MAX_LEN=17,VALUE=\"\""), &orientationCharId);
```

Once we are done with the setup, we write a function to sense and publish the three
orientation values on our orientation GATT service. We publish new values on an GATT
characteristic with the command AT+GATTCHAR.

```cpp
void orientation() {
  // Get Euler angle data
  imu::Vector<3> euler_vector = bno.getVector(Adafruit_BNO055::VECTOR_EULER)
  float angleX = euler_vector.x();
  float angleY = euler_vector.y();
  float angleZ = euler_vector.z();
  
  // Command is sent when \n (\r) or println is called
  // AT+GATTCHAR=CharacteristicID,value
  ble.print( F("AT+GATTCHAR=") );
  ble.print( orientationCharId );
  ble.print( F(",") );
  ble.print(String(angleX));
  ble.print( F(",") );
  ble.print(String(angleY));
  ble.print( F(",") );
  ble.println(String(angleZ));
}
```

Finally, the loop() is continuously calling orientation(), check for error and wait
the amount of time specify for the data collection frequency.

```cpp
void loop(void) {

  orientation();

  // Check if command executed OK
  if ( !ble.waitForOK() ) {
    error(F("Failed to get response!"));
  }

  // Delay before next measurement update
  delay(BNO055_SAMPLERATE_DELAY_MS);
}
```

The complete source code is available in
<a href="https://github.com/datacentricdesign/wheelchair-design-platform/tree/master/examples/communication/bluetooth/bno055_gatt_orientation" target="_blank">examples /
communication / bluetooth / bno055_gatt</a>

### 3.3 Wire and set up on the Wheel

We can see a simple wiring example using this board, together with an IMU (in our
case the BNO055):



Flash the code on the Feather 32u4 and connect to your orientation service from
your phone.

Set up the power bank and the breadboard on the wheel.

## 4 Python

The next step is to subscribe to the GATT service from the Raspberry Pi and push
the received data on the DCD Hub.

Let's connect to the Raspberry Pi and install the Bluetooth dependencies for Python.
Once logged on the Raspberry Pi, type in the following commands to install BLE dependencies.

```bash
sudo apt-get install bluez libbluetooth-dev

sudo pip3 install git+https://github.com/peplin/pygatt

sudo pip3 install "pygatt[GATTTOOL]"

sudo pip3 install bluepy

sudo pip3 install pexpect
```

We can use the command 'blescan' to scan the Bluetooth devices around. This way,
you can retrieve your Feather 32u4 with its name and identify its MAC address.

```bash
sudo blescan
```

Copy the MAC address and paste in your .env file as a new environment variable
'BLUETOOTH_DEVICE_MAC', for example:

blescan

```bash
BLUETOOTH_DEVICE_MAC=fb:48:5b:84:36:4a
```

Then, copy the example

```bash
cp examples/communication/bluetooth/subscribe_gatt_orentation.py wheelchair/
```

Let's have a look to this Python code. Has usual, we start by importing libraries
and loading environment variable (note the extra one for the Bluetooth MAC address).

Then we need to define which GATT service we want to connect to. Thus we create a
constant with the UUID of our orientation service.

```python
GATT_CHARACTERISTIC_ORIENTATION = "MY_GATT_ORIENTATION_SERVICE_UUID"
```

We define a 'handler', a method which will be called every time new data is coming
in for our orientation characteristic. In this method, we read the data, transform
the string into an array of three values, then update the property.

```python
def handle_orientation_data(handle, value_bytes):
    """
    handle -- integer, characteristic read handle the data was received on
    value_bytes -- bytearray, the data returned in the notification
    """
    print("Received data: %s (handle %d)" % (str(value_bytes), handle))
    values = [float(x) for x in value_bytes.decode('utf-8').split(",")]
    find_or_create("Left Wheel Orientation",
                   PropertyType.THREE_DIMENSIONS).update_values(values)
```

Finally, we use the pygatt library to connect to the device and subscribe to the
orientation characteristic.

```python
# Start a BLE adapter
bleAdapter = pygatt.GATTToolBackend()
bleAdapter.start()

# Use the BLE adapter to connect to our device
left_wheel = bleAdapter.connect(BLUETOOTH_DEVICE_MAC, address_type=ADDRESS_TYPE)

# Subscribe to the GATT service
left_wheel.subscribe(GATT_CHARACTERISTIC_ORIENTATION,
                     callback=handle_orientation_data)
```

## 5 Local Pre-Processing

To go further, you can have a look at the second example orientation_rotation which
show an example of a service with two characteristics.

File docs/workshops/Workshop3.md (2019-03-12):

# Workshop 3: Actuators

In this workshop we lead you step-by-step to implement three actuators (vibration
motors, LEDs and speakers) from data, through Bluetooth and from the cloud.

1. [Rotation to Vibration](#1-nudging-for-recommended-limit)
2. [LED GATT Service on the Wheel](#2-internet-status-on-the-wheel)

## 1 Nudging for Recommended Limit

At the end of workshop 2, we were able to register to a BLE GATT service on the
Feather 32u4 placed on the left wheel of the wheelchair to receive orientation
and rotation data. In this step, we explore how we can use this information to
reason on the Raspberry Pi, and trigger action on the Arduino Mega.



### 1.1 Vibration pattern

Let's start with a look at the vibration motor describe here:
[Vibration Motor](../resources/actuators/vibration_motors.md)

Building on the couple of examples we provide, write your own vibration pattern.

### 1.2 Vibration Function

The next step is to transform this continuous pattern into a function that we
can turn on and off on demand. Thus, we create a function vibration_pattern() and
we move our code from loop() to vibration_pattern(). In loop, we call vibration_pattern()
and leave a delay between each loop. This transformation gives us the possibility
to implement multiple vibration patterns (one per function).

```cpp
void vibration_pattern() {
  if (increase) {
    i+=10;  // incrementing the power of the vibration motor
  } else {
    i-=10;
  }

  if ( i > 255) {
    increase = false;
  } else if ( i < 127) {
    increase = true;
  }
}

void loop() {
  vibration_pattern();
  delay(50);
}
```

### 1.2 Writing over Serial

Now that we have a function, we can better control whether the vibration motor is
on or off. Let's create a variable 'vibration_enabled' at the top of the file (next
to 'i' and 'increase') and set it to false.

```cpp
boolean vibration_enabled = false;
```

Then, in loop(), we want to listen to commands sent via the Serial connection (in this case
through the USB cable). We use Serial.read(), which gives us the last character received
via Serial. Let's define that sending:

* '1' means 'turn on'
* '0' means 'turn off'

For every loop, we check whether we receive a 1 or a 0 and change vibration_enabled
accordingly. This looks as follows:

```cpp
void loop() {
  char command = Serial.read();
  if (command == '1') {
    Serial.println("Turning on Vibration...");
    vibration_enabled = true;
  } else if (command == '0') {
    Serial.println("Turning off Vibration...");
    vibration_enabled = false;
    analogWrite(VIB_PIN, 0);
  }
  if (vibration_enabled) {
    vibration_pattern();
    analogWrite(VIB_PIN, i);
  }
  delay(50);
}
```

### 1.3 Control from Python

The next step is to control this vibration from Python. The following example
shows how to establish a serial connection and write (i.e. send) messages. In this
case, we send '1' (turning on the vibration) then wait for 5 seconds before sending
'0' (turning off the vibration). We wait another 2 seconds and start again.
Notice the added "encode()" function. This is because the write() function on serial can only write binary data. By writing '1', we're sending a string. The encode() is there to convert from the string type to binary. 

```python
# Import required library
import os                       # To access environment variables
from dotenv import load_dotenv  # To load environment variables from .env file
import serial                   # To connect via the serial port
import time                     # To sleep for a few seconds

# The thing ID and access token
load_dotenv()

# Start reading the serial port
ser = serial.Serial(
    port = os.environ['SERIAL'],
    baudrate = 9600,
    write_timeout = 0)

while True:
    ser.write('1'.encode())
    time.sleep(5)
    ser.write('0'.encode())
    time.sleep(2)
```

### 1.4 Data-Driven Vibration

The final step is to control the vibration based on data. In this example, we will
nudge the wheelchair users when they reach their recommended number of wheel rotations.

To do this, we can start from the last example of workshop 2, which subscribes to
orientation and rotation GATT services from the wheel and sends the data to the DCD Hub.
We remove the subscription to orientation, which is not necessary in this case. We modify
the handler of rotation data so that we check whether we need to nudge the wheelchair user or not.

You can find a complete example in
<a href="https://github.com/datacentricdesign/wheelchair-design-platform/blob/master/examples/actuators/vibration_motors/vibrate_rotation_excess.py" target="_blank">
examples/actuators/vibration_motors/vibrate_rotation_excess.py</a>

## 2 Internet Status on the Wheel

In this second part, we want to communicate the Internet connection status: is
the wheelchair connected to the cloud?

We will use an RGB diffuse LED as indicator on the wheel. The Raspberry Pi will
check for the Internet availability. We will create a BLE GATT service to WRITE
(i.e send) commands to the Feather 32u4 on the wheel, to turn on/off the LED
depending on the internet status.



### 2.1 Diffused LEDs

The first step is to explore how to wire and control a NeoPixel 5mm Diffused LED.
This is described in the LED page in section 3:
[/resources/actuators/leds](../resources/actuators/leds.md#3-neopixel-5mm-diffused-led)

### 2.2 Internet Connection status

In many case, checking the Internet connection is not enough, we want to know
whether the cloud we rely on is currently available. Most cloud services have
a 'health' API in order to check if the service is available and running fine.
For the DCD Hub, it is /health, you can try in your web browser:

<a href="https://dwd.tudelft.nl/api/health" target="_blank">https://dwd.tudelft.nl/api/health</a>

The result should look as follows:

Health API

Notice the two information of the result, a status number (0 if everything is running
properly) and a message. Let's create a Python script that runs this HTTP request
to check the DCD Hub status. In your wheelchair folder, create a file dcd_hub.py
and write the following code.

```python
import requests

def dcd_hub_status():
    """
    Return the DCD Hub status:
    - 0: Connection successful
    - 1: Could not reach the hub (Connection or Hub issue)
    """

    uri = "https://dwd.tudelft.nl/api/health"
    try:
        json_result = requests.get(uri).json()
        if json_result["status"] is 0:
            # We received a response with status = 0, everything is fine
            return 0
        # In any other case, there is a issue
        return 1
    except Exception as e:
        # Show some information about the error
        print(str(e))
        # Return 1, the connection wasn't successful
        return 1
```

This code import the 'requests' library, convenient to make a HTTP request. We
declare a function dcd-hub_status() which try to call the health API and return
0 if it succeed. If it failed because of the Internet connection or the availability
of the Hub, then it return 1.

try/except (also known as try/catch in other languages) is a construction that makes
your code more robust. You define in the 'try' something that work but sometimes
can fail. In our case, firing an HTTP request fails if there is no Internet
connection. If the code in the try clause fails, then the except clause is executed.
In our case, we print the error and return '1', avoiding our code to crash.

Notice we create this function in a separate file. Doing so give you the opportunity
to import it anywhere in your code without rewriting nor copy/pasting it.

### 2.3 GATT Service for Control

For this step we will need the latest version of our Feather's firmware. The
firmware is software that is embedded in a piece of hardware, typically provided
by its manufacturer. Adafruit provides a convenient way to update it with an
Android or iOS app:
<a href="https://learn.adafruit.com/adafruit-feather-32u4-bluefruit-le/dfu-bluefruit-updates" target="_blank">
https://learn.adafruit.com/adafruit-feather-32u4-bluefruit-le/dfu-bluefruit-updates</a>

Then, open examples/communication/bluetooth/gatt_write in the Arduino IDE. This
code is an example of GATT service enabling to WRITE (i.e. the Feather receive
data) in contrast with the previous section in which we were READ (i.e. the
Feather was sending data). Read through the code to understand what it does, then
flash it on the Feather.

On the Raspberry Pi, you can run examples/communication/bluetooth/write_gatt.py
This code connect to your Feather via Bluetooth and use the code discussed previously
to check the connection. If the connection with the DCD Hub can be established, it
writes on the LED GATT service to turn on the LED, otherwise it writes to turn off
the LED.

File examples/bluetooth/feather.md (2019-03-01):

# Adafruit Feathers
The Adafruit Feather is a complete line of development boards that are both standalone and stackable.

## Bluetooth
Bluetooth is a wireless technology standard for exchanging data over short distances using short-wavelength UHF radio waves (ISM band of the wave spectrum - from 2.400 to 2.485 GHz).
From these waves, that originate from fixed and mobile devices, PANs (personal area networks) are built.

**BTLE**
Bluetooth Low Energy is a new low-power, 2.4GHz spectrum wireless protocol. In particular, its the only wireless protocol that you can use with iOS without needing special certification and it's supported by all modern smart phones. This makes it excellent for use in portable projects that will make use of an iOS or Android phone or tablet. It also is supported in Mac OS X and Windows 8+.
### PANs
A personal area network (PAN) is a computer network for interconnecting devices centered on an individual person's workspace. A PAN provides data transmission amongst devices such as computers, smartphones, tablets and personal digital assistants.

PANs can be used for communication amongst the personal devices themselves, or for connecting to a higher level network and the Internet where one master device takes up the role as gateway. A PAN may be wireless or carried over wired interfaces such as USB.

A wireless personal area network (WPAN) is a PAN carried over a low-powered, short-distance wireless network technologies such as Bluetooth. The reach of a WPAN varies from a few centimeters to a few meters.

### Adafruit Feather 32u4 Bluefruit
The Adafruit Feather 32u4 Bluefruit is an 'all-in-one' Arduino-compatible + Bluetooth Low Energy(BLTE) board with built in USB and battery charging. It's an Adafruit Feather 32u4 with a BTLE module.



#### Pins
1. **BAT** - positive voltage to/from JST jack for optional Li-Po battery;
2. **EN** - 3.3V regulator's enable pin. has pull up, connect to ground to disable regulator;
3. **USB** - Positive voltage to/from microUSB jack, if connected;
4. **Pins 13-5**
    * **.a** - GP(General Purpose)I/O 13, can do PWM output, is connected to red LED next to USB port;
    * **.b** - GP I/O 12, also analog input A11;
    * **.c** - GP I/O 11, can do PWM output;
    * **.d** - GP I/O 10, can do PWM output and can also be analog input A10;
    * **.e** - GP I/O 9, can do PWM output and can also be analog input A9, analog input is connected to a  voltage divider for Li-Po battery, so naturally 'sits' at 2V DC due to the resistor divider;
    * **.f** - GP I/O 6, can do PWM output and can also be analog input A7;
    * **.g** - GP I/O 5, can also do PWM output;
5. **SCL** - GP I/O 3, can do PWM output , and act as interrupt 0. Also the I2C clock pin, has no pullup by default, so when using I2C, may need 2.2-10kΩ pullup;
6. **SDA** -  GP I/O 2, can do PWM output , and act as interrupt 1. Also the I2C data pin, has no pullup by default, so when using I2C, may need 2.2-10kΩ pullup;
7. **RST** - Reset pin, can be tied to ground to manually reset the AVR, as well as launch the bootloader manually;
8. **3V** - Output from 3.3V regulator, supplies 500mA at peak;
9. **ARf** - ARef, the analog reference pin. Normally the reference voltage is the same as the chip logic voltage (3.3V). If an alternative analog reference is needed, the pin must be connected to it, and then,  the external AREF in the firmware needs to be selected. Upper limit of (3.3V);
10. **GND** - Common Ground for the board;
11. **A0-A5** - Analog as well as digital I/O pins;
12. **SCK** - SPI clock input pin, should be kept available for the bluefruit;
13. **MOSI** - SPI Master Out - Slave In pin, should be kept available for the bluefruit, can also be used to reprogram the chip with an AVR(family of microcontrollers) programmer;
14. **MISO** - SPI Master In - Slave Out pin, used by Bluefruit LE module, should be kept available for the bluefruit;
15. **0 RX** - GP I/O 0, can also receive (input) pin for Serial 1, and interrupt 2;
16. **1 TX** - GP I/O 1, can also receive (output) pin for Serial 1, and interrupt 3;
17. **DFU** - Force-DFU (device firmware upgrade) pin for over-the-air updates to the Bluefruit module. Most likely will not be used, so, in general, keep disconnected (but it is available).

#### Technical details
The main structure of this board specifies a main processor (which is an ATmega32u4 in our case) and a co-processor module which is the red and silver rectangle, containing an nRF51 chip which can only do Bluetooth Low Energy.

The nRF51 is programmed with the Bluefruit firmware, and can be controlled with AT commands over an SPI connection. When the main processor (32u4) wants to send or receive BLE(Bluetooth Low Energy) data, it sends commands to the co-processor module. However, this solution can only act as a peripheral, not as a central device, it has a  bit more power draw, does not take advantage of the newer nRF52 capabilities, and cannot use bluetooth classic.
This board can be connected to 3.7V Li-Po batteries or the through the USB port.It will automatically switch over to USB power when its available.

* ATmega32u4 processor @ 8MHz with 3.3V logic/power;
* 3.3V regulator with 500mA peak current output;
* USB native support, comes with USB bootloader and serial port debugging;
* 20x GPIO pins;
* Hardware Serial, I2C, and SPI support;
* 7x PWM pins;
* 10x analog inputs
* Built in 100mA lipoly (lithium polymer) charger with charging status indicator LED;
* Pin #13 connected to red LED for general purpose blinking;
* Power/enable pin;
* Reset button;

Whenever we want to have sensors wirelessly sending data, we will use this board as its µcontroller. For that, we can start with setting up how to add this board to the Arduino IDE.

#### Setup with Arduino IDE

Inside of the Arduino IDE, we can go to Arduino -> Preferences (circled in red):



Once inside the Preferences menu we will have to add an additional Board Manager URL. We will do that by pressing the button (circled in Red):



Note that each link should be in a separate row (in case you have other board URLs installed).
The link you should add (without quotes) is: "https://adafruit.github.io/arduino-board-index/package_adafruit_index.json".



After pressing ok, we can now head into the Boards Manager ( Tools -> Board:... -> Boards Manager...):



Once inside we will search "Adafruit", and the Adafruit AVR Boards package should appear. We will then install the latest version. This package contains a bunch of AVR boards from Adafruit, including our own Feather:



After this, we should have our Adafruit Feather 32u4 Board available in the boards submenu option (Tools -> Board:... -> Adafruit Feather 32u4):



After selecting it, we should be ready to compile code for, and flash it through the Arduino IDE! This board is fully compatible with Arduino, so the code in the Arduino examples can be used (with only some minor port and power wiring adaptations, as this is a 3.3V board, and also has less ports than the mega) :



#### Example Schematic

We can see a simple wiring example using this board, together with an IMU (in our case the BNO055):



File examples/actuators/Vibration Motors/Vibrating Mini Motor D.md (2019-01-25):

# Vibration Motors
## Vibrating Mini Motor D

This Adafruit vibration motor can take voltages from 2V up to 5V, where it will draw from 40mA to 100mA. It will reach speeds of 11k RPM at its peak.  If your circuit can provide more than 100mA, be sure to prevent against it with the use of resistors in series (refer to LED tutorial).



* Red wire - Vcc;
* Blue wire - Ground;

###Examples

#### PWM control of the vibration motor
In this code example we're going to apply PWM (refer to the LED tutorial) to control the strength of this motor.

##### Schematic
The wires are thin, so make sure they are well connected to the breadboard!



##### Results
In the end you should see something like this!



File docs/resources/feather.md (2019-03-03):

# Adafruit Feathers
The Adafruit Feather is a complete line of development boards that are both 
standalone and stackable.

## Bluetooth
Bluetooth is a wireless technology standard for exchanging data over short 
distances using short-wavelength UHF radio waves (ISM band of the wave spectrum
- from 2.400 to 2.485 GHz). From these waves, that originate from fixed and
mobile devices, PANs (personal area networks) are built.

**BTLE**
Bluetooth Low Energy is a new low-power, 2.4GHz spectrum wireless protocol. In 
particular, its the only wireless protocol that you can use with iOS without
needing special certification and it's supported by all modern smart phones.
This makes it excellent for use in portable projects that will make use of an
iOS or Android phone or tablet. It also is supported in Mac OS X and Windows 8+.

### PANs
A personal area network (PAN) is a computer network for interconnecting devices
centered on an individual person's workspace. A PAN provides data transmission
amongst devices such as computers, smartphones, tablets and personal digital
assistants.

PANs can be used for communication amongst the personal devices themselves, or
for connecting to a higher level network and the Internet where one master
device takes up the role as gateway. A PAN may be wireless or carried over
wired interfaces such as USB.

A wireless personal area network (WPAN) is a PAN carried over a low-powered,
short-distance wireless network technologies such as Bluetooth. The reach of a
WPAN varies from a few centimeters to a few meters.

### Adafruit Feather 32u4 Bluefruit
The Adafruit Feather 32u4 Bluefruit is an 'all-in-one' Arduino-compatible + Bluetooth
Low Energy(BLTE) board with built in USB and battery charging. It's an Adafruit
Feather 32u4 with a BTLE module.



#### Pins
1. **BAT** - positive voltage to/from JST jack for optional Li-Po battery;
2. **EN** - 3.3V regulator's enable pin. has pull up, connect to ground 
to disable regulator;
3. **USB** - Positive voltage to/from microUSB jack, if connected;
4. **Pins 13-5**
    * **.a** - GP(General Purpose)I/O 13, can do PWM output, is connected to red
    LED next to USB port;
    * **.b** - GP I/O 12, also analog input A11;
    * **.c** - GP I/O 11, can do PWM output;
    * **.d** - GP I/O 10, can do PWM output and can also be analog input A10;
    * **.e** - GP I/O 9, can do PWM output and can also be analog input A9,
    analog input is connected to a  voltage divider for Li-Po battery, so naturally
    'sits' at 2V DC due to the resistor divider;
    * **.f** - GP I/O 6, can do PWM output and can also be analog input A7;
    * **.g** - GP I/O 5, can also do PWM output;
5. **SCL** - GP I/O 3, can do PWM output , and act as interrupt 0. Also the I2C
clock pin, has no pullup by default, so when using I2C, may need 2.2-10kΩ pullup;
6. **SDA** -  GP I/O 2, can do PWM output , and act as interrupt 1. Also the I2C
data pin, has no pullup by default, so when using I2C, may need 2.2-10kΩ pullup;
7. **RST** - Reset pin, can be tied to ground to manually reset the AVR, as well
as launch the bootloader manually;
8. **3V** - Output from 3.3V regulator, supplies 500mA at peak;
9. **ARf** - ARef, the analog reference pin. Normally the reference voltage is
the same as the chip logic voltage (3.3V). If an alternative analog reference
is needed, the pin must be connected to it, and then,  the external AREF in the
firmware needs to be selected. Upper limit of (3.3V);
10. **GND** - Common Ground for the board;
11. **A0-A5** - Analog as well as digital I/O pins;
12. **SCK** - SPI clock input pin, should be kept available for the bluefruit;
13. **MOSI** - SPI Master Out - Slave In pin, should be kept available for the
bluefruit, can also be used to reprogram the chip with an AVR(family of 
microcontrollers) programmer;
14. **MISO** - SPI Master In - Slave Out pin, used by Bluefruit LE module,
should be kept available for the bluefruit;
15. **0 RX** - GP I/O 0, can also receive (input) pin for Serial 1, and interrupt 2;
16. **1 TX** - GP I/O 1, can also receive (output) pin for Serial 1, and interrupt 3;
17. **DFU** - Force-DFU (device firmware upgrade) pin for over-the-air updates
to the Bluefruit module. Most likely will not be used, so, in general, keep
disconnected (but it is available).

#### Technical details
The main structure of this board specifies a main processor (which is an ATmega32u4
in our case) and a co-processor module which is the red and silver rectangle,
containing an nRF51 chip which can only do Bluetooth Low Energy.

The nRF51 is programmed with the Bluefruit firmware, and can be controlled with AT
commands over an SPI connection. When the main processor (32u4) wants to send or
receive BLE(Bluetooth Low Energy) data, it sends commands to the co-processor
module. However, this solution can only act as a peripheral, not as a central
device, it has a  bit more power draw, does not take advantage of the newer nRF52
capabilities, and cannot use bluetooth classic.
This board can be connected to 3.7V Li-Po batteries or the through the USB port.
It will automatically switch over to USB power when its available.

* ATmega32u4 processor @ 8MHz with 3.3V logic/power;
* 3.3V regulator with 500mA peak current output;
* USB native support, comes with USB bootloader and serial port debugging;
* 20x GPIO pins;
* Hardware Serial, I2C, and SPI support;
* 7x PWM pins;
* 10x analog inputs
* Built in 100mA lipoly (lithium polymer) charger with charging status indicator LED;
* Pin #13 connected to red LED for general purpose blinking;
* Power/enable pin;
* Reset button;

Whenever we want to have sensors wirelessly sending data, we will use this board
as its µcontroller. For that, we can start with setting up how to add this board
to the Arduino IDE.

#### Setup with Arduino IDE

Inside of the Arduino IDE, we can go to Arduino -> Preferences (circled in red):



Once inside the Preferences menu we will have to add an additional Board Manager
URL. We will do that by pressing the button (circled in Red):



Note that each link should be in a separate row (in case you have other board URLs
installed). The link you should add (without quotes) is:
"https://adafruit.github.io/arduino-board-index/package_adafruit_index.json".



After pressing ok, we can now head into the Boards Manager ( Tools > Board:... >
Boards Manager...):



Once inside we will search "Adafruit", and the Adafruit AVR Boards package should 
appear. We will then install the latest version. This package contains a bunch of
AVR boards from Adafruit, including our own Feather:



After this, we should have our Adafruit Feather 32u4 Board available in the boards
submenu option (Tools -> Board:... -> Adafruit Feather 32u4):



After selecting it, we should be ready to compile code for, and flash it through
the Arduino IDE! This board is fully compatible with Arduino, so the code in the
Arduino examples can be used (with only some minor port and power wiring adaptations,
as this is a 3.3V board, and also has less ports than the mega) :



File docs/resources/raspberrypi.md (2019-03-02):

# Some Raspberry Pi settings

* <a href="http://www.diegoacuna.me/how-to-run-a-script-as-a-service-in-raspberry-pi-raspbian-jessie/" target="_blank">Run your program as a service</a>

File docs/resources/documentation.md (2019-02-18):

# Documenting your Prototype

A key element of your prototype is its documentation: what is it? What can it do
and how? The documentation will get people to understand your design, contribute
to your code and help you make your prototype useful.

Here are a few starting points:

* README.md: an important file at the root of your project where you describe
what this is all about, how to use your project, what test you have done, who 
contributed, etc. <a href="https://github.com/matiassingers/awesome-readme">
A list of examples and articles here.</a>

* Change Log is a another useful file to communicate about the major changes and
milestones your project. <a href="https://keepachangelog.com/en/1.0.0/" target="_blank">
Some guidances about Change logs here.</a>

* Nice looking website out of your markdown with 
<a href="https://keepachangelog.com/en/1.0.0/" target="_blank">GitHub Pages</a>.
For example, this website has been automatically generated from the
wheelchair-design-platform repository.

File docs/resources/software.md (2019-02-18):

# Software resources

Here are some suggested website and books to get started with programming environments

## Python

<a href="http://www.learnpython.org/" target="_blank">http://www.learnpython.org/</a>

## Arduino

<a href="https://create.arduino.cc/projecthub" target="_blank">https://create.arduino.cc/projecthub</a>

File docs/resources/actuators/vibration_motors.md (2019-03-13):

# Vibration Motors

## Vibrating Mini Motor D

This Adafruit vibration motor can take voltages from 2V up to 5V, where it will draw from 40mA to 100mA. It will reach speeds of 11k RPM at its peak.  If your circuit can provide more than 100mA, be sure to prevent against it with the use of resistors in series (refer to LED tutorial).



* Red wire - Vcc;
* Blue wire - Ground;

### Examples

#### PWM control of the vibration motor
In this code example we're going to apply PWM (refer to the LED tutorial) to control the strength of this motor.

##### Schematic

The wires are thin, so make sure they are well connected to the breadboard!



Examples of code be found here: 
<a href="https://github.com/datacentricdesign/wheelchair-design-platform/tree/master/examples/actuators/vibration_motors" target="_blank">/examples/actuators/vibration_motors</a>

##### Results

In the end you should see something like this!



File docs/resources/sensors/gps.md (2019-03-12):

# GPS Positional Sensors
GPS (Global Positioning System) is a global satellite-based radio navigation system, composed of a satellite system that provides geolocation and time information to a GPS receiver anywhere on or near the Earth where there is an unobstructed line of sight to four or more GPS satellites. These signals are relatively weak, and obstacles such as Buildings or mountains can block them.

GPS does not require the user to transmit any data, and it operates independently of any telephonic or internet reception, though these technologies can enhance the usefulness of the GPS positioning information.



## Adafruit Ultimate GPS Breakout v3

This breakout is built around the MTK3339 chipset, a high-quality GPS module that can track up to 22 satellites on 66 channels, has an high-sensitivity receiver (-165 dBm tracking), and a built-in antenna. It can do up to 10 location updates a second for high speed, high sensitivity logging or tracking. Power usage is low, at around 20mA during navigation.



### Pins
1. **3.3v** - Clean 3.3V output from internal voltage regulator, supplies at least 100mA, if needed;
2. **EN** -  Enable pin, has a 10K pull up resistor. When this pin is pulled to ground, it will turn off the GPS module. Handy for very low power projects where you want to easily turn the module off for long periods. You will lose your fix if you disable the GPS and it will also take a long time to get fix back if you don't have the backup battery installed;
3. **VBAT** - Input pin, connected to the GPS real time clock battery backup. Using the battery spot on the back is suggested, but if you have a project with a coin cell or another kind of battery that you want to use (and its under 3.3V) you can connect it to the VBAT pin;
4. **FIX** - Output pin, same pin as the one that drives the red LED. When there is no fix, the FIX pin pulses up and down once every second. When there is a fix, the pin is low (0V) for most of the time, and once every 15 seconds it will pulse high for 200 milliseconds;
5. **TX** - Serial data pin, that transmits data from the GPS module to your microcontroller/computer. It uses 3.3V logic levels. Data comes out at 9600 baud by default;
6. **RX** - Serial data pin used to send data to the GPS. Can be used with 3.3V or 5V logic, there is a logic level shifter. By default it expects 9600 baud data, which has to be sent to it checksum'med with NMEA (combined electrical and data specification for communication between marine electronics such as echo sounder, sonars, anemometer, gyrocompass, autopilot, GPS receivers a) sentences;
7. **Gnd** - common power and signal ground;
8. **Vin** - Power input, to be connected to 3-5VDC. GPS's are very sensitive, so is important to have a nice and quiet power supply. Don't connect to a switching supply if you can avoid it, also, an LDO (Low-dropout regulator) will be less noisy;
9. **PPS** - Output pin. It is a "pulse per second" type of output. Most of the time it is at logic low (ground) and then it pulses high (3.3V) once a second, for 50-100ms, so it should be easy for a microcontroller to sync up to it.

### Technical Details
The data logging of this GPS module functions like this:
The time, date, longitude, latitude, and height is logged every 15 seconds and only when there is a fix. The internal FLASH can store about 16 hours of data, and it will automatically append data so you don't have to worry about accidentally losing data if power is lost. It is not possible to change what is logged and how often, as its hardcoded into the module, but this arrangement covers many of the most common GPS data logging requirements.

* 1-10 Hz update rate;
* Tracking of up to 22 satellites on 66 channels;
* Position Accuracy of 1.8 meters;
* Velocity Accuracy of 0.1 meters/s;
* Warm/cold start up time of 34 seconds;
* Acquisition sensitivity of -145 dBm;
* Tracking sensitivity of -165 dBm;
* Maximum Velocity of 515m/s;
* Operating current of 25mA when tracking, 20 mA current draw during navigation;
* Outputs NMEA 0183, 9600 baud (default);
* DGPS (differential global positioning system)/WAAS (Wide Area Augmentation System)/EGNOS (European Geostationary Navigation Overlay Service) support;
* Up to 210 PRN (pseudorandom noise number) channels (used to identify satellites);
* Jammer detection and reduction;
* Multi-path detection and compensation;
* RTC battery-compatible;
* Built-in data logging, only requires microcontroller to send the "Start Logging" command, after that, it can go to sleep and does not need to wake up to talk to the GPS anymore;
* PPS output on fix;
* Internal patch antenna + u.FL connector for external active antenna (module will automatically detect the active antenna and switch over);
* Fix status LED;

#### Battery Backup
This breakout has a built in real time clock (RTC), which can keep track of time even when it power is lost and it doesn't have a fix yet. It can also help reduce fix times, if you expect to have an unreliable power connection(like solar, for example). To use the RTC, we need to attach a battery. There is a spot on the back for a CR1220 sized battery holder. You can use any 12mm coin cell - these are a popular and common form factor:



Once the GPS loses power, it will revert to the factory default for baud rates, configuration, etc. A backup battery will prevent that!

The backup real-time-clock circuitry draws 7 uA (0.007 mA) so a CR1220 will last 40mAh / 0.007mA = 5,714 hours = 240 days continuously. The backup battery is only used when there's no main 3V power to the GPS, so as long as it's only used as backup once in a while, it can last years.

### Examples

#### Output Raw GPS Serial data, bypassing Arduino.

GPS modules will start 'spitting' data, and trying to get a 'fix' (location verification) the moment you turn them on. Like most other GPS modules, the Adafruit Ultimate GPS uses TTL serial output to send data.

Knowing this, a good way to test it is to wire it directly to the computer via the TTL serial to USB converter on an Arduino(RX and TX pins). You can also use an FTDI Friend or another TTL adapter.

##### Schematic



For this example, we'll just flash the Arduino with an empty sketch, turn on the Serial monitor (please select to 9600 baud on the serial monitor window), and watch the GPS "NMEA sentence" output from the module data come in.

##### Results
Let's see our console output:



**Note** that the data you receive is separated by commas. If you get empty values between the commas, that means that the module doesn't have a fix, and the red LED should be blinking. To get a fix, you should have the module pointed towards the sky uninterrupted for some time, out of a window or preferably outside.

The most common sentences people use are the GPRMC (Global Positioning Recommended Minimum Coordinates) and the GPGGA sentences.

These provide the time, date, latitude, longitude, altitude, estimated land speed, and fix type. Fix type indicates whether the GPS has locked onto the satellite data and received enough data to determine the location (2D fix) or location+altitude (3D fix).

<details><summary>Click this to expand an explanation of the GPRMC sentence.</summary>
<p>

This line is called the RMC (Recommended Minimum) sentence and it has the most useful data. Each chunk of data is separated by a comma.

* The first part is the current time in GMT (Greenwich Mean Time). The first two numbers indicate the hour, the next two are the minutes, then the next two are the seconds. Finally, we have the milliseconds;

* The second part is the 'status code', if it is a V that means the data is Void (invalid). If it is an A that means its Active (the GPS could get a lock/fix);

* The next 4 pieces of data are the geolocation data.
To look at this location in Google maps,  it requires you to use +/- instead of N-S W-E notation. N and E are positive, S and W are negative.
The geolocation data is in degrees and minutes in the following format: Latitude: DDMM.MMMM (The first two characters are the degrees) Longitude: DDDMM.MMMM (The first three characters are the degrees);

* The next data field is the ground speed in knots;

* The next data point is the tracking angle, this is meant to approximate what 'compass' direction we're heading at based on our past travel;

* The one after that is 160412 which is the current date (DDMMYY);

* At the end, there is the \*XX data which is used as a data transfer checksum (for transfer error debugging).

</p>
</details>

#### Echoing Raw GPS Data with the Arduino

In this example, we will echo the raw GPS data using the Arduino. For this the installation of the Adafruit GPS library is required.
Be very careful in respect to the schematic, as in this case, you'll be connecting **TX** from the GPS breakout to the corresponding **RXx** port of the Arduino. In this particular example,  RX(GPS) -> TX1(Mega)) & TX(GPS) -> RX1(mega). Be sure to set the Serial console's window baud rate to 115200.

##### Schematic



##### Results
Let's see our console output:



#### Parsing GPS Data with the Arduino

This time we will parse the data using the Arduino. For this the installation of the Adafruit GPS library is required.
Be very careful in respect to the schematic, as in this case, you'll be connecting **TX** from the GPS breakout to the corresponding **RXx** port of the Arduino. In this particular example,  RX(GPS) -> TX1(Mega)) & TX(GPS) -> RX1(mega). Be sure to set the Serial console's window baud rate to 115200.

##### Schematic



##### Results
Let's see our console output:



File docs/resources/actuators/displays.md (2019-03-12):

# Displays

## Color TFT LCD displays

TCT LCD (Thin-film-transistor liquid-crystal display) is a variant of LCD, that uses TFT tech to improve image quality.

### 1.8" Color TFT LCD display with MicroSD Card Breakout

Possessing 128 * 160 color pixels true TFT with full 18-bit color, this display can be used with any microcontroller.

There's internal logic that ensures you can use this  with 3.3 or 5v power and logic. They also have a microSD card holder for easy loading of Full Color Bitmaps, as long as the microSD is formatted with Fat16/32.

Lets start by knowing what each pin on the breakout does:



1. **Lite** - PWM input for the backlight control. Connect to 3-5VDC to turn on, to ground to turn it off or, you can PWM for intensity of the blacklight;
2. **MISO** - this is the SPI Master In - Slave Out pin, used for the SD card. It isn't used for the TFT display which is write-only;
3. **SCLK** - SPI clock input pin;
4. **MOSI** - SPI Master Out - Slave In pin, it is used to send data from the microcontroller to the SD card and/or TFT;
5. **TFT_CS** - TFT SPI chip select pin;
6. **Card_CS** - SD card chip select, used if you want to read from the SD card;
7. **D/C** - TFT SPI data or command selector pin;
8. **RST** - TFT reset pin. Connect to ground to reset the TFT! (It's best to have this pin controlled by the library so the display is reset cleanly, but you can also connect it to the Arduino Reset pin, which works for most cases) ;
9. **Vcc** - Power pin, connect to 3-5V DC - it has reverse polarity protection, however try to wire properly!
10. **GND** - Power and signal ground pi.

This color display uses SPI (Serial Peripheral Interface) to receive image data. That means you need at least 4 pins - clock, data in, TFT_CS and D/C. If you'd like to have SD card usage too, you need another 2 pins.

### SPI

Serial Peripheral Interface, is a common communication protocol for 2-way comms between 2 devices.
The master can talk to any slave on the bus, but each slave can only talk to the master.
Each slave on the bus has its own unique slave select signal. The master will use these signals to select which slave it is talking to.

SPI sets a clock signal, so the devices don't have to agree on a data rate beforehand (like you do with Serial by setting up Serial.begin() ), the clock only has to be lower than the max frequency for all devices involved.

#### Standard SPI bus
Consisting of 4 signals:
* Common to all devices:
  * Master Out Slave In (MOSI) - Master line for sending data to the peripheral;
  * Master In Slave Out (MISO) - Slave line for sending data to the master;
  * the clock (SCK) - synchronize data transmission generated by the master.
* Specific line for each device:
  * Slave Select (SS) -  pin on each device that the master can use to enable and disable that specific device.

#### SPI with Arduino
First of all; MISO, MOSI, and SCK are available in a consistent physical location on the ICSP header:



You can find the places for the headers in this schematic of the Mega, although you can also use some (specific) digital pins. the white dot means its the pin number 1 of ICSP. You can then refer to these pins as ICSP-1, 2, etc:



### Examples
In this section, we'll go over two basic examples, to learn the basics of using this screen with the Arduino.

First of all, you will need to install the following two libraries:
* Adafruit GFX (a graphics library);
* Adafruit_ST7735 (a library for the display).

#### TFT Screen Graphics Test
In this first example, let's run through all of the available graphics drawing functions of the Adafruit GFX library!

##### Schematic



###### Pins of the Screen Breakout (left to right):
* Gnd;
* Backlight (connect to Vcc);
* TFT Reset pin (connect to a digital pin, 3 in this case);
* TFT SPI data pin (connect to a digital pin, 4 in this case);
* Card CS, (connect to a digital pin, 5 in this case)
* TFT CS, (connect to a digital pin, 2 in this case);
* MOSI, (connect to SPI MOSI Hardware pin (SCPI-4));
* Clock, (connect to SPI Clock hardware pin (SCPI-3));
* Not used!
* Vcc pin.

##### Results
Once you've run the example program, you should see this in your serial!


#### Display Images on the TFT Screen by using a microSD card

In this program, we'll be displaying images in the screen (in bitmap image format)!
We will use the previous libraries, and Arduino's SD library!

Start by converting some images to 160x128 24bit color bitmap format, and placing them in a FAT16/32 formatted microSD card, and placing that in the SD card holder. You can find some bitmap files in the Example folder, and put those in the SD card

##### Schematic



###### Pins of the Screen Breakout (left to right):
* Gnd;
* Backlight (connect to Vcc);
* TFT Reset pin (connect to a digital pin, 3 in this case);
* TFT SPI data pin (connect to a digital pin, 4 in this case);
* Not used!
* TFT CS, (connect to a digital pin, 2 in this case);
* MOSI, (connect to SPI MOSI Hardware pin (SCPI-4));
* Clock, (connect to SPI Clock hardware pin (SCPI-3));
* MISO pin (connect to MISO hardware pin (SCPI-1));
* Vcc pin.

#####  Results
You should see this in your console at the end!



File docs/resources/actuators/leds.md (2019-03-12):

# LEDs

## 1 LEDs

An LED is a type of diode that emits light. A diode is, simply, a device that lets
current go through it in one direction, but resists it in the other. To pass current
through the diode in the direction it does not resist (anode to cathode), you need
to supply some voltage to it. An LED normally spends from 1.8 to 3.3 volts, depending
on the particular type, this is called its voltage drop or forward voltage. The
current that the LED spends nominally is called forward current.  With LEDs you
have to be careful  to not supply too much current to an LED, or else you might
fry it!.

That's why you'll see that normally you have a resistor in series with the LED,
to assure that not too much current goes through it.



By knowing the forward current and voltage of an LED, and the available power
source's voltage, you can calculate how big the resistor you apply in series
should be. the formula is a simple derivation of Ω's law (V = RI).

Rs = ( Vcc - Vf ) / If
1. Rs = Resistance in series with LED;
2. Vcc = power source's voltage;
3. Vf = forward  voltage of the LED;
4. If = forward current of the LED.

If you have several LEDs in series with similar forward currents, you can simply
replace Vf with the sum of all forward voltages of the LEDs.

## 2 PWM

The last thing we should know with LEDs, is that you can not only turn them on
and off, but also vary their intensity. You can do so by controlling the voltage
supplied to the LED, but that is a morose and finicky process. Instead, you can
use a technique called PWM,(Pulse Width Modulation); in which, instead of always
powering the LED at full blast, we providing a very high frequency square wave of
voltage, in which the pulses  are such that, on average, the device is x% on,
and 100-x% off.  Such is termed the duty cycle. (a duty cycle of 50% means the
signal is 50% on, and 50 % off, in average).

By doing this, we are alternating between having the LED on, and off, but so quickly
that our eyes "average" the result! So an LED with a duty cycle of 25% looks 25%
as bright as the normal LED! Notice that all of this is done digitally, so,
essentially PWM is a way of getting analog like results with digital means.



You can use PWM with the pins that have the tag PWM in Arduino, and can use the
function analogWrite() for establishing the duty cycle on a pin that can use PWM,
with a value from 0 (0%) to 255 (100%).

Below, you can see the pins you can use with PWM!



### Examples

Let's do some examples with the types of LEDs (and buttons) we have.

### Simple LED with button switch.

We'll be making a simple circuit to turn on the LED, with the help of the push button.

We'll be using a simple LED, so lets use a 220Ω resistor (this will work just fine
for a most LEDs), together with the 5v output of the Arduino.

#### Schematic:



### Simple LED with Pulsing intensity using PWM

We'll make a simple circuit to make a pulsing LED, with the help of some code
this time!

#### Schematic:



#### Result



## 3 NeoPixel 5mm Diffused LED

The NeoPixel Diffused LED is a special type of LED with 24bit color which gives
256 intensities for R, G and B, allowing for a lot of colors. This requires the
use of the NeoPixel library for Arduino.

Lets see the pins and what they're for:

NeoPixel 5mm Diffused LED

1. Data In, where we connect our arduino data pin (and a 470 Ω resistor);
2. Vcc input pin, (5v);
3. Ground;
4. Data out, where we can chain several NeoPixel LEDs together(simply connect
the data in port of one to the data out of the other).

#### Important Notes

* When connecting several NeoPixels Through-the-hole individual LEDs in a chain,
it is advisable to add a 0.1 µF capacitor between the + (Vcc) and – (Ground) pins
of *EACH PIXEL*.

* Adding a ~470 Ω resistor between your microcontroller's data pin and the data
input on the first NeoPixel LED can help prevent voltage spikes on the data line
that can damage it. Also the Arduino shouldn't be able to power more than a few
(8 ~ish) NeoPixels directly from the 5V pin.

* After 1-2 meters distance from the Arduino to the first NeoPixel, the signal
starts to degrade, and becomes unreliable.

* Avoid connecting NeoPixels to a live circuit. If you must, always connect
ground first, then +5V, then data. Disconnect in the reverse order.

* If powering the pixels with a separate supply, apply power to the pixels before
applying power to the microcontroller.

* NeoPixels powered by 5v require a 5V data signal. If using a 3.3V microcontroller
you must use a logic level shifter

* If your microcontroller and NeoPixels are powered from two different sources
(e.g. separate batteries for each), there must be a ground connection between
the two.

#### Schematic

This example was made with two LEDs, you can of course choose how many you want,
taking care you're feeding them enough current and voltage.

Schematic Diffused LEDs

You can find the code for this example here:
<a href="https://github.com/datacentricdesign/wheelchair-design-platform/blob/master/examples/actuators/leds/diffused_led/diffused_led.ino" target="_blank">Diffused LED example</a>

#### Result

This is how your serial should look like!

Result Diffused LEDs

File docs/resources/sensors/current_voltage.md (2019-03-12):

# Current & Voltage Sensors

These are Integrated sensors that detect both the current, and the voltage (then, following Ohm's law, the power) of a circuit.

The most common method for measuring currents in electronic circuits is to place low-value sense resistors in series with the load and measure the voltage drop across them.

## INA219 High Side DC Current Sensor

This breakout board allows for power monitoring, including both a High side voltage and DC current draw sensor over I2C.

High-side and low-side current sensing refers to the placement of the current-sense resistor:
* High Side - between the positive supply and the load (whatever is being driven by the circuit);
* Low Side - between the load and ground.



### Pins
1. Ground;
2. Vcc, power with 5V;
3. SDA data pin;
4. SCL clock pin;
5. Vin- terminal (if you want to use another current sensor);
6. Vin+ terminal (if you want to use another current sensor);
7. Vin- of INA219 DC current sensor;
8. Vin+ of INA219 DC current sensor;

### Technical Details
* 1% precision;
* High Side measurement, up to +26V DC;
* Powered with 3-5V;
* Uses precision amplifier to measure voltage across 0.1Ω , 1% sense resistor;
* Can measure up to ±3.2A (since internal amplifier has maximum input resolution of ±320mV);
* Internal 12bit ADC( Analog to Digital converter);
* Resolution  of 0.8mA at ±3.2A range.

This breakout requires the use of the library Adafruit INA219.

Now lets see a list of terms for the sensor:
* Bus voltage - voltage between GND and V-, total voltage seen by circuit under test. (supply voltage - shunt voltage);
* Shunt voltage - voltage between V- and V+, voltage drop across the shunt resistor;

### Examples

#### Power sensor of a simple Circuit
We'll be making use of all the basic functionalities of this breakout to do some simple measurements of a basic circuit!

##### Schematic



##### Results
Now, let's see what our console should look like:



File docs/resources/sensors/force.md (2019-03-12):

# Force Sensing Resistors (FSRs)
FSRs are a type of robust polymer thick film (PTF) that decrease in resistance with an increase of force applied to the surface of the sensor. We will be Working with the interlink FSR 406.
The interlink is part of the single zone FSRs family, with optimized force sensitivity for use in human touch control of electronic devices.



## Technical Details

* Sensitivity range from 0.1N to 100N of force;
* 0.45mm thick;
* Handles up to 10M actuations;
* 10MΩ when non actuated;
* Non linear Resistor, so changes of force are not linear to changes in resistance, especially in the end of the sensing range (~4V and up);

## Examples

### Pressure Sensor with Sampling and Basic Filtering
Lets make a pressure sensor using a voltage divider circuit and the arduino!

#### Schematic
The common way to use this transducer is with the use of a voltage divider circuit. $R_1$'s value will change the way the voltage curve(for $V_1$ ) is for different pressures (the lower the resistance,  the more low pressure values are spread out, and the curve becomes more 'stretched'), lets see a common voltage divider, and our particular case:



Here's the whole sensor system diagram:



#### Results
Let's see what the console looks like in the end!



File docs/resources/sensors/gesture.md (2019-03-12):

# Proximity, Light, RGB, and Gesture Sensors

## Adafruit APDS9960

This breakout has a lot of integrated sensors, and allows the addition of basic gesture sensing (left, up, down, right), RGB color sensing (detect amount of R, G, B light), proximity sensing (how close an object is to the front of the sensor), and Ambient light sensing (how much clear light).



### Pins
1.  Vin, (3-5V);
2.  3.3V output from internal voltage regulator, may supply up to 100mA, if needed;
3.  Gnd;
4.  SCL, clock pin of I2C;
5.  SDA, data pin of I2C;
6.  Interrupt output pin, can be used to detect new reading is ready, gets too high, or gets too low;
7. Proximity detection up to ≈ 15-20cm.

This breakout uses the Library Adafruit APDS9960 library.

### Technical Details
* Can be used with both 3.3 and 5v µcontrollers;
* Has Integrated IR LED driver, with 4 directional photodiodes;
* Proximity sensor for objects in front of sensor (up to a few centimeters), with 8bit resolution;
* With 4 IR sensors, changes in light reflectance in each cardinal direction can be measured and used for gesture detection;
* Possesses configurable interrupt that can fire when a proximity threshold is broken, or when a color sensor reaches a certain threshold.

### Examples

#### Gestures
In this example we're going to test the gesture features of the board!

##### Schematic


##### Results


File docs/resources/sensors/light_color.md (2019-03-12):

# Light and color

## Adafruit APDS9960

This breakout has a lot of integrated sensors, and allows the addition of basic gesture sensing (left, up, down, right), RGB color sensing (detect amount of R, G, B light), proximity sensing (how close an object is to the front of the sensor), and Ambient light sensing (how much clear light).



### Pins
1. Vin, (3-5V);
2. 3.3V output from internal voltage regulator, may supply up to 100mA, if needed;
3. Gnd;
4. SCL, clock pin of I2C;
5. SDA, data pin of I2C;
6. Interrupt output pin, can be used to detect new reading is ready, gets too high, or gets too low;
7. Proximity detection up to ≈ 15-20cm.

This breakout uses the Library Adafruit APDS9960 library.

### Technical Details
* Can be used with both 3.3 and 5v µcontrollers;
* Has Integrated IR LED driver, with 4 directional photodiodes;
* Proximity sensor for objects in front of sensor (up to a few centimeters), with 8bit resolution;
* With 4 IR sensors, changes in light reflectance in each cardinal direction can be measured and used for gesture detection;
* Possesses configurable interrupt that can fire when a proximity threshold is broken, or when a color sensor reaches a certain threshold.

### RGBC Color Sensing
In this example we're going to test the RGB color sensing features of the board!

#### Schematic


#### Results


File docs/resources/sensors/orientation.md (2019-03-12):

# Orientation Sensors

These sensors serve to provide orientation data, and they normally mix several
different sensors such as accelerometers, gyroscopes and magnetometers.

## BNO055 Intelligent 9-axis absolute orientation sensor



This 9-DOF (Degrees of freedom) sensor turns the sensor data from an accelerometer,
gyroscope and magnetometer into 3D space orientation.
These so called sensor fusion algorithms that blend accelerometer, magnetometer and
gyroscope data into stable three-axis orientation output can be difficult to
implement on low cost real time systems.

The BNO055 manages to get this right by taking a MEMS (Microelectromechanical
systems) accelerometer, magnetometer and gyroscope and putting them on a single
die with a high speed ARM Cortex-M0 based processor to process all the sensor data,
abstract away sensor fusion and real time requirements, and output data you can
use in quaternions, Euler angles or vectors.

### Technical details

This Sensor will require the use of the Adafruit Unified Sensor (Adafruit_Sensor),
and Adafruit BNO055 libraries.

The data from this board can be accessed in several formats, namely:

* Absolute Orientation (Euler Vector, 100Hz) - Three axis orientation data based on a 360° sphere;
* Absolute Orientation (Quaternion, 100Hz) - Four point quaternion output for more accurate data manipulation;
* Angular Velocity Vector (100Hz) - Three axis of 'rotation speed' in rad/s;
* Acceleration Vector (100Hz) - Three axis of acceleration (gravity + linear motion) in m/s^2;
* Magnetic Field Strength Vector (20Hz) - Three axis of magnetic field sensing in micro Tesla (uT);
* Linear Acceleration Vector (100Hz) - Three axis of linear acceleration data (acceleration minus gravity) in m/s^2;
* Gravity Vector (100Hz) - Three axis of gravitational acceleration (minus any movement) in m/s^2;
* Temperature (1Hz) - Ambient temperature in degrees celsius;

### Pins

Now, lets see what each pin of this board is for:



* **Vin** - 3.3-5.0V power supply input;
* **3vo** - 3.3V output from internal voltage regulator, may supply up to 500mA, if needed;
* **GND** - The common/GND pin;
* **SDA** - I2C data pin, can be used with 3V or 5V logic, and there's a 10K pullup on this pin;
* **SCL** -  I2C clock pin, can be used with 3V or 5V logic, and there's a 10K pullup on this pin;
* **RST** - 5V safe hardware reset pin. Can be set to low, then high to cause a reset on the sensor;
* **PS0 & PS1** - These pins can be used to change the mode of the device (it can
also do HID-I2C (HID (Human interface device) over I2C) and UART (Universal asynchronous
receiver-transmitter)), and also are provided in case Bosch provides a firmware update
at some point for the ARM Cortex M0 MCU inside the sensor. They should normally
be left unconnected;
* **INT** - 3V voltage level hardware interrupt output pin, can be configured to
generate an interrupt signal upon certain events, like movement detected by the
accelerometer, etc. (not currently supported in the Adafruit library, but the chip
and HW (hardware) is capable of generating this signal);
* **ADR** - this pin can be set to high to change the default I2C address for the
BNO055, if you need to connect two ICs on the same I2C bus. The default address is
0x28. If this pin is connected to 3V, the address will be 0x29.

### Examples

##### Schematic (for all examples)



#### Basic Three Axis orientation data (in Euler angles)

In this example, simple orientation data in the form of Euler Angles is given.

##### Euler Angles

Euler angles are three angles introduced by Leonhard Euler to describe the
orientation of a rigid body with respect to a fixed coordinate system.
Any orientation can be achieved by composing three elemental rotations, i.e.
rotations about the axes of a coordinate system. Euler angles can be defined
by three of these rotations.

<a href="https://github.com/datacentricdesign/wheelchair-design-platform/tree/master/examples/sensors/orientation/bno055_euler_angles" target="_blank">Source code</a>

###### Geometrical definition

The axes of the original frame are denoted as x, y, z and the axes of the rotated
frame as X, Y, Z. The geometrical definition (sometimes referred to as static)
begins by defining the line of nodes as the intersection of the planes xy and XY.



Using it, the three Euler angles can be defined as follows:
 ⍺ (or φ) β- is the angle between the x axis and the N axis (x-convention - it
 could also be defined between y and N, called y-convention).
 * β (or ϴ) is the angle between the z axis and the Z axis.
 * ɣ (or Ψ) is the angle between the N axis and the X axis (x-convention).

##### Results
Here's how your console should look in the end:



#### Basic Three Axis raw data

In this example, all types of possible raw data from the IMU are given.

<a href="https://github.com/datacentricdesign/wheelchair-design-platform/tree/master/examples/sensors/orientation/bno055_raw_data" target="_blank">Source code</a>

##### Results
Here's how your console should look in the end:



#### Basic Rotation calculations

In this example, the total number of rotations, both forward and reverse since
the beginning of the activation of the IMU are computed.

<a href="https://github.com/datacentricdesign/wheelchair-design-platform/tree/master/examples/sensors/orientation/bno055_rotations" target="_blank">Source code</a>

##### Results
Here's how your console should look in the end:



## Sparkfun RGB rotary encoder

Encoders can measure the rotation of a shaft. There are two main types of encoders:

* Absolute - this type of encoders relate information about the absolute position
of the shaft;
* Incremental - this type of encoders relate information on the relative motion
of the shaft of the encoder, i.e. changes in the position of its shaft, but not
its absolute position.

The Sparkfun RGB rotary encoder is one of the most common types for general
electronics, a quadrature rotary encoder (a type of incremental encoder), and is
rather similar to a potentiometer; however its rotation is infinite in both
directions. It also possesses full RGB illumination of the shaft, with the shaft
also doubling as a clickable button.

### Functionality

This encoder is conveniently soldered into a breakout board, for easy use with a
breadboard and access of its I/O.  With the help of the following diagram we can
see how this encoder works.



1. B contact, one of the data pins;
2. "Common" contact - to be connected to ground;
3. A contact, another of the data pins;
4. Input to Red LED;
5. Input to Green LED;
6. "Switch" contact, LOW by default, switches to HIGH when shaft is clicked;
7. Input to Blue LED;
8. "Vcc" connector, to be connected to 3.3V.

Let's review how an rotary encoder works:


The incremental rotary encoder works in a very simple way. There are 3 terminals,
where C is the common, which is connected to ground. The rotary encoder also has
metallic contacts connected to VCC. As you can see, the data pins are phased 
between each other, and during the turning of the wheel, when the pin touches 
the contact it will be 1, and 0 for when it touches the ground. The data streams 
are shifted 90˚(hence quadrature) from each other (since there's a particular 
distance between the contacts).
Why use two data streams? Well to figure out which direction we're turning it, 
since you can tell which data stream comes first!

#### Diagram of the circuit
Here follows a diagram of a test circuit using the Arduino Mega.
The LEDS  current is 25 mA. They have the following forward voltages(voltage
drop), so if you are using a different Vcc than 5V, you must calculate other
resistances (check the LED tutorial):

R : 2V
G : 3.3V
B : 3.3V



#### Results

Now you should have a working RGB encoder! Below you can find what your serial
output should look like:



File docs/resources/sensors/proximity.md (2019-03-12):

# Proximity Sensors

## Infrared Proximity Sensors

IR sensors are proximity sensors that use  Infrared rays to  measure distance to 
objects. This is done by blasting the ray, catching the reflection and calculating 
the distance between the two objects! Can be used for detecting objects, obstacle 
detection, and other applications!

###  Sharp GP2Y0A02YK0F Long Range

This IR proximity sensor made by Sharp is good for sensing objects up to 1.5m 
away and, in our case, comes with a Japanese Solderless Terminal(JST) connector.
This connector has three wires:

* Red - to connect to $V_{cc}$;
* Black - to connect to Ground;
* Yellow - Analog Output.

#### Technical Details



* Supply voltage  between [4.5 - 5.5]V;
* Analog output 2.8V (15 cm), to 0.4V(150cm);
* Distance Measuring Range [20 - 150]cm;
* Non linear (exponential) relation between distance and voltage;
* Consumption current : Typ. 33 mA;

Just like we did with the Pressure Sensor, the relation between distance and 
voltage is also not linear. A curve fitting was done over measured distances 
to have an estimate of the distance from the voltage measurements.

#### Examples

##### Proximity sensor
We will make a simple proximity sensor, with continuous distance measurements:

###### Schematic


###### Results
This is how your console should look like!



## Adafruit APDS9960

This breakout has a lot of integrated sensors, and allows the addition of basic
gesture sensing (left, up, down, right), RGB color sensing (detect amount of R, 
G, B light), proximity sensing (how close an object is to the front of the 
sensor), and Ambient light sensing (how much clear light).



### Pins
1.  Vin, (3-5V);
2.  3.3V output from internal voltage regulator, may supply up to 100mA, if needed;
3.  Gnd;
4.  SCL, clock pin of I2C;
5.  SDA, data pin of I2C;
6.  Interrupt output pin, can be used to detect new reading is ready, gets too high, or gets too low;
7. Proximity detection up to ≈ 15-20cm.

This breakout uses the Library Adafruit APDS9960 library.

### Technical Details
* Can be used with both 3.3 and 5v µcontrollers;
* Has Integrated IR LED driver, with 4 directional photodiodes;
* Proximity sensor for objects in front of sensor (up to a few centimeters), with 8bit resolution;
* With 4 IR sensors, changes in light reflectance in each cardinal direction can be measured and used for gesture detection;
* Possesses configurable interrupt that can fire when a proximity threshold is broken, or when a color sensor reaches a certain threshold.

#### Proximity sensor
In this example we're going to test the proximity features of the board!

##### Schematic


##### Results


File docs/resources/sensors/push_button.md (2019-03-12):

# Pushbutton Switch

A pushbutton switch, is a very simple electronic device with 4 pins. When left
to itself (open), there is no electrical connection between the two sets of pins.
When a switch is pressed, it will close its metallic contact on the two sets of
pins, thus allowing current to pass between the 2 sets of 2 pins.

Here's a brief schematic (note, a set of pins means those pins are always connected,
you can see the sets in black, and the mechanism to join them electrically when
you press the button in red):

Push Button Schematic

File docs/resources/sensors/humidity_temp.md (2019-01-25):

# DHT22 (Humidity and temperature sensor)

This basic, low cost digital sensor is simple to use, outputting digital signal data on the data pin, however, you can only get new data from it every 2 seconds. It requires no analog inputs.

If you are connecting several, each must have its own data pin.

##Technical Details
Please use a 4.7 - 10 kΩ medium strength pullup resistor between pins 1 and 2.  



* **Pins**
  1. Vcc, connect to 5V;
  2. Data Output pin  (digital);
  3. Not used;
  4. Ground.

* **Characteristics**
  * 3-5 V power and I/O;
  * 0 to 100% humidity readings range (2-5% accuracy);
  * -40˚ to 80˚ temperature readings range (±.5˚ accuracy);
  * Sampling rate 0.5Hz (2 secs per new data point).

## Examples
To use this sensor with the Arduino, please install the following libraries;
* Adafruit Unified Sensor;
* DHT sensor library.

### Simple Humidity and temperature reader
#### Schematic
Here's how our example circuit is going to look like:



#### Results
Lets see how the console will look with the finished example:



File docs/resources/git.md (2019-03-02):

# Git & Github

Git is a version control system (VCS). It helps to keep track of all the  changes
in your project and sharing these. While it is heavily used by software developers to
track and share code, it is also useful to track and share the progress of any
design or research process. The principle is as follows: you share a remote
repository, you 'pull' the latest changes (any files, code, doc...) from your
peers from this repository, you make changes on your machine, and you 'push' your
changes on the remote repository, making them available to your peers.

Here are four short videos with more details:
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

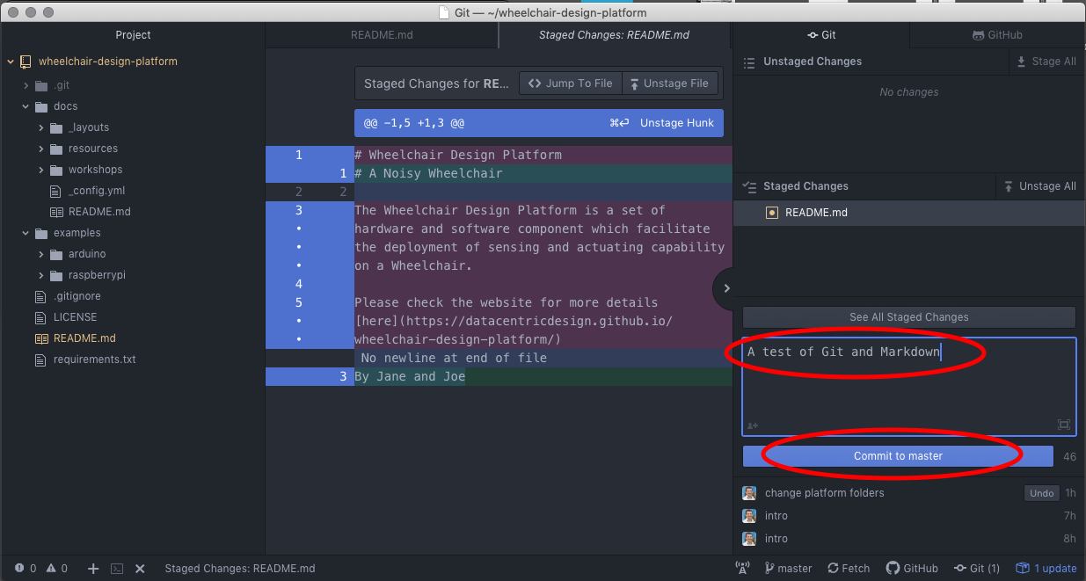
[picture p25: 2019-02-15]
docs/resources/images/git_commit.png

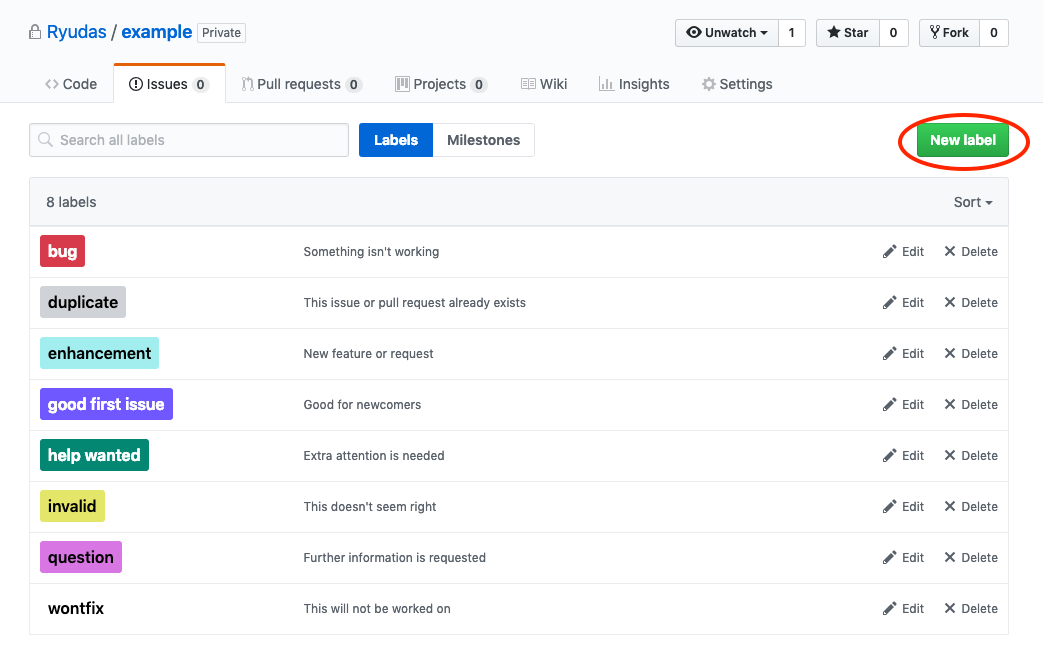
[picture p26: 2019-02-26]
docs/resources/images/git_3.png

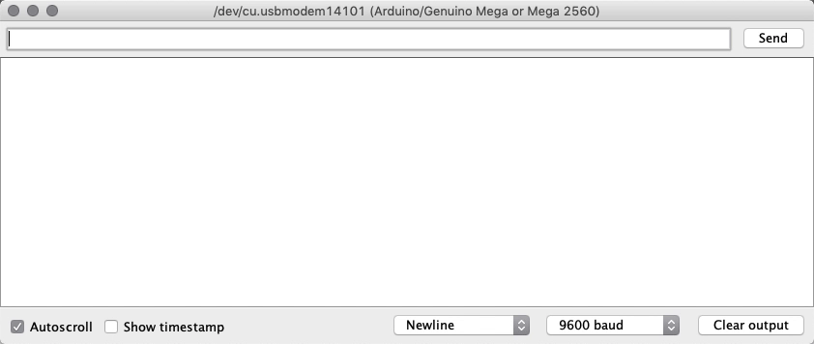
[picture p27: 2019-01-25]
docs/resources/sensors/images/humidity_temp_1.gif

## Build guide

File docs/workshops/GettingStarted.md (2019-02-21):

# Getting Started

In this tutorial, you will setup a development environment for Python and Arduino.

## 1. Atom

The first tool we need is a code editor, commonly called IDE (integrated
development editor). For this we will use Atom, as it is open source and popular
for its modularity.

Download and start Atom <a href="https://atom.io/" target="_blank">here</a>.

Atom has the typical features of an IDE, we will go through them during this workshop.
The first of them is the terminal. A terminal is a text-based interface we use
to enter and execute commands on a computer. While we will maximize the use of
graphical tools, we will also use the terminal in some occasions.

On the top menu, go to Packages > Settings View > Install Packages/Themes

Search for 'terminal plus' and install the first one 'platformio-ide-terminal'

Now you can open a terminal by clicking on the + sign in the bottom left corner.

## 2. Python

Python is the main programming language we will use throughout this course. To
execute Python code on your machine, you need to install a Python interpreter.
We will use Python 3.x (as opposed to 2.x).

In Atom, open a terminal and type in the following command to check if Python is
installed on your laptop with the appropriate version.

On Mac, type in

```bash
python3 --version
```

On Windows, type in:

```bash
python --version
```

If Python 3 is installed, the result should look as follows:

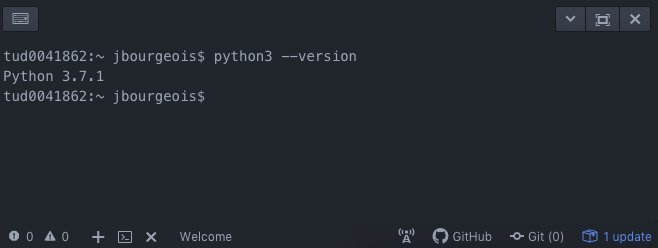
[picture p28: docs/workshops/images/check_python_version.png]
Flowchart Push Button


If the command results are 'Command Not found' (or an equivalent message), you need
to install Python 3. Otherwise, skip to section 2.2.

### 2.1 Install Python

Select, download and install the latest version of Python 3 for your system
<a href="https://www.python.org/downloads/release/python-372/" target="_blank">here</a>.

#### Windows

Once installed, go to 'Start > System > Properties > Advanced System Properties >
Environment Variable' In User Variables, double click on 'Path'. At the end of
the line, add a semi-colon (;<zero-width space>), followed by:

C:\Users\YOUR_USERNAME\AppData\Local\Programs\Python\Python37;C:\Users\YOUR_USERNAME\AppData\Local\Programs\Python\Python37\Scripts

(Replace YOUR_USERNAME with your Windows user name)

Close and reopen the Atom to check the installation, by typing in your console:

```bash
python --version
```

And verifying that the correct version of python was installed.

#### Mac

After installation, close and reopen the Atom to check if it was successful, by typing the following on your console:

```bash
python3 --version
```

if the correct version of python is shown, the install was successful.

### 2.2 Python Dependencies

In the Python ecosystem, Pip is a tool that manages packages for us. We will use
it to install and update any Python library our project relies on. You can check whether
Pip is already install with the following command.

On Mac, type in:

```bash
python3 -m pip --version
```
On Windows, type in:

```bash
python -m pip --version
```

If it is not found, you can install it as follows.

On Mac, type in:

```bash
python3 get-pip.py
```

On Windows, download the file <a href="https://bootstrap.pypa.io/get-pip.py" target="_blank">get-pip.py</a>
and save it (CMD+S or Ctrl+S) in your Downloads folder. In the Atom terminal, type in the
following command:

```bash
python Downloads\get-pip.py
```

### 2.3 Python in Atom

The next step is the Python plugin for Atom, to get some help specifically for
Python in Atom. Go to the terminal and type:

On Mac, type in:

```bash
python3 -m pip install 'python-language-server[all]'
```

On Windows, type in:

```bash
python -m pip install 'python-language-server[all]'
```

When it is installed, on the top menu of Atom, click on *'Packages' >
'Settings View' > 'Install Packages/Themes'*. Search and install 'atom-ide-ui'
and 'ide-python'.

If you do not have experience with Python, we recommend you to go through the following tutorial
to get started: <a href="http://www.learnpython.org/" target="_blank">http://www.learnpython.org/</a>

## 3 Git & GitHub

Git is a version control system (VCS). It helps to keep track of all the  changes
in your project and sharing these. While it is heavily used by software developers to
track and share code, it is also useful to track and share the progress of any
design or research process. The principle is as follows: you share a remote
repository, you 'pull' the latest changes (any files, code, doc...) from your
peers from this repository, you make changes on your machine, and you 'push' your
changes on the remote repository, making them available to your peers.

Here are four short videos with more details:

* <a href="https://git-scm.com/video/what-is-version-control" target="_blank">What is version control</a>
* <a href="https://git-scm.com/video/what-is-git" target="_blank">What is git</a>
* <a href="https://git-scm.com/video/get-going" target="_blank">Get Going</a>
* <a href="https://git-scm.com/video/quick-wins" target="_blank">Quick wins</a>

### 3.1 Install Git

Download and install Git from <a href="https://git-scm.com/download" target="_blank">here</a>.

GitHub is a popular online platform that hosts remote Git repositories.
We will use it throughout the course to host your repo.

### 3.2 Sign up on GitHub

If you do not have GitHub account, sign up
<a href="https://github.com/" target="_blank">here</a>.

## 4 Install Arduino IDE

Similar to Atom, the Arduino IDE is an editor with a convenient set of tools to program
Arduino-like devices. You can download and install the latest version from
<a href="https://www.arduino.cc/en/Main/Software" target="_blank">here</a>.

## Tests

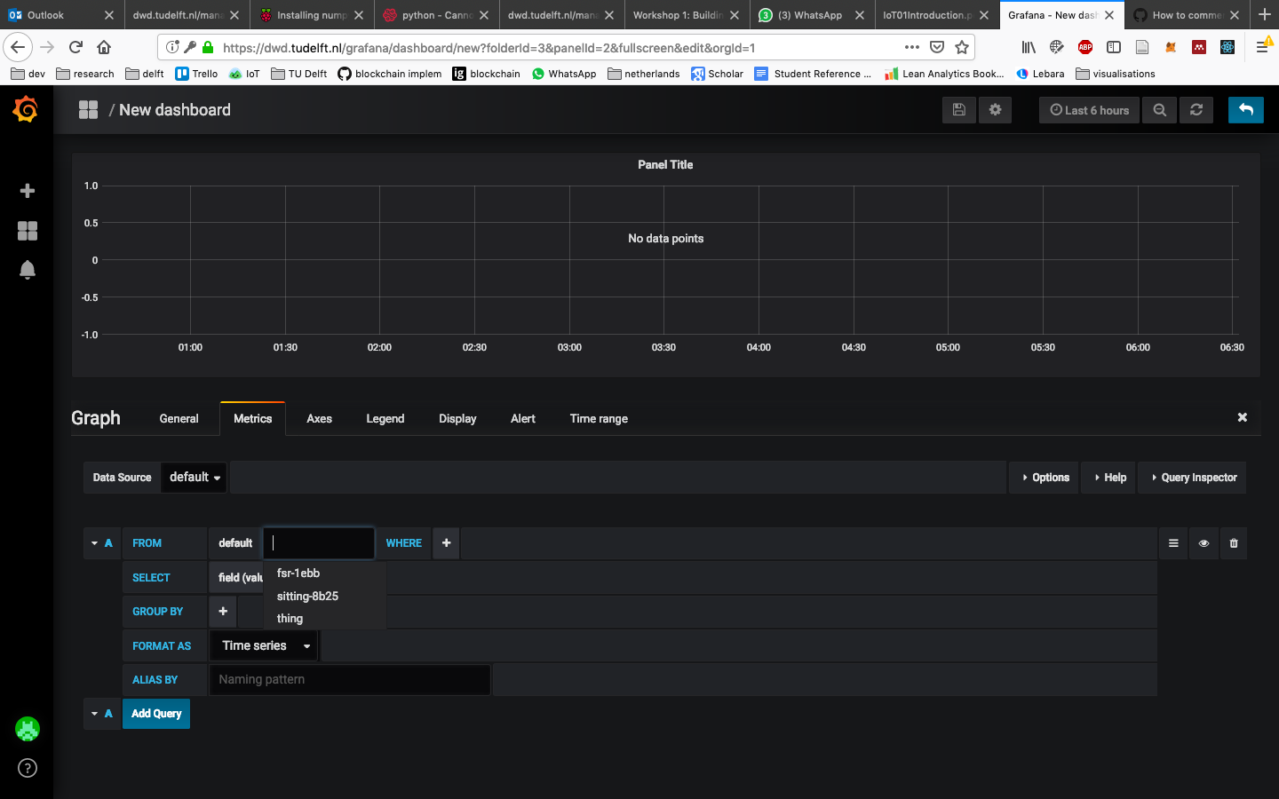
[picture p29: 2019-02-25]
docs/workshops/images/grafana_measurement.png

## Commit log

2019-01-17 LED basics
2019-01-17 Added simple LED examples
2019-01-17 Minor formatting changes to the LEDS and Buttons, helper text
2019-01-17 Added Instructions on the Neopixel diffused LEDs
2019-01-17 Minor formatting changes to LEDs readme
2019-01-17 Replaced wrong image in LEDs and Buttons readme
2019-01-18 Added diffused LED example
2019-01-18 Finished content of full LEDS and Buttons Document
2019-01-24 Added Vibration motor example
2019-01-25 Added Readme on Vibration motors
2019-01-25 Added DHT Humidity and Temperature sensor readme
2019-01-25 Finalized all explanations of DTH sensor
2019-01-25 Added pressure sensor readme
2019-01-28 Added code example with adaptive filtering and calibrated curve fitting
2019-01-28 Added IR proximity sensors Readme
2019-01-28 Added code example for IR Sensor
2019-01-28 Added curve fitting and simple filtering to IR code Example
2019-01-29 Finished Readme for the IR sensors
2019-01-29 Minor Formatting changes to code in IR sensor
2019-01-31 Major reformatting of Sensors and Actuators folder
2019-01-31 Added initial readme on IN219 powersensor
2019-02-01 Fixed minor formatting of APDS9960 sensor
2019-02-12 Added Orientation Sensors readme
2019-02-12 Added relevant pinout details for orientation sensor
2019-02-22 Added fritzing
    [FSR.fzz]
2019-02-25 Update Workshop1.md
    Changed ssh connection from Windows to Powershell instead of Putty.
2019-02-26 Fixed LED workshop 1 code example
2019-03-01 moving Git flow in git tuto
2019-03-01 Added Setup up for the feather with the Arduino IDE
2019-03-02 reorganising doc
    [FSR.fzz]
2019-03-04 Configured proper error LED pin
2019-03-04 GATT UUID example is more clearly stated
    altered to a more clear sample that the gatt service code is clearly stated
2019-03-08 Added breakdown of RAW EMEA data sample
2019-03-09 split code / doc and load sensor/actuator examples on website
    [force.fzz]
2019-03-10 refactor led / button pages
2019-03-11 Change LED Pin
    In tune with the schematic at https://datacentricdesign.github.io/wheelchair-design-platform/resources/actuators/leds.html#schematic-2
2019-03-12 Removed redundant folder in sensor examples
2019-03-13 fixed broken link in vibration motor
2023-02-20 remote print raw values
